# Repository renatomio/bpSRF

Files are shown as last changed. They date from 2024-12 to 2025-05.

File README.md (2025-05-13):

# bpSRF: An extra robotic finger powered by wrist movements
 Github site for the bpSRF, a body-powered supernumerary robotic finger for hand augmentation that requires no electronic components.
## Project Overview
This guide introduces the assembly and operation of the **Body-Powered Supernumerary Robotic Finger (bpSRF)**. The bpSRF is an lightweight device designed to enhance users' grasping capabilities by controlling an additional robotic finger using wrist movements. Unlike conventional SRFs, the bpSRF eliminates the need for electronic components and relies solely on body-powered mechanisms.

<p align="center">
  The bpSRF
</p>

The device is particularly suited for helping people with hand impairments that limit finger but not wrist movements. It is also an excellent tool for healthy individuals seeking to explore additional degrees of freedom and novel hand grasping patterns. The bpSRF is easily manufacturable using 3D printing, making it a cost-effective and replicable solution.

<p align="center">
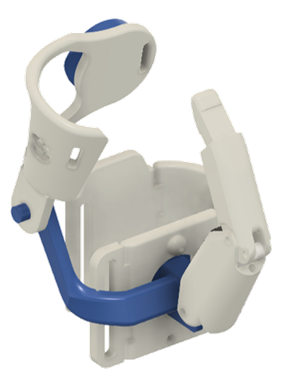
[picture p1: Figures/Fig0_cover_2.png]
  
</p>

Here are some examples on how it can be used:

<p align="center">
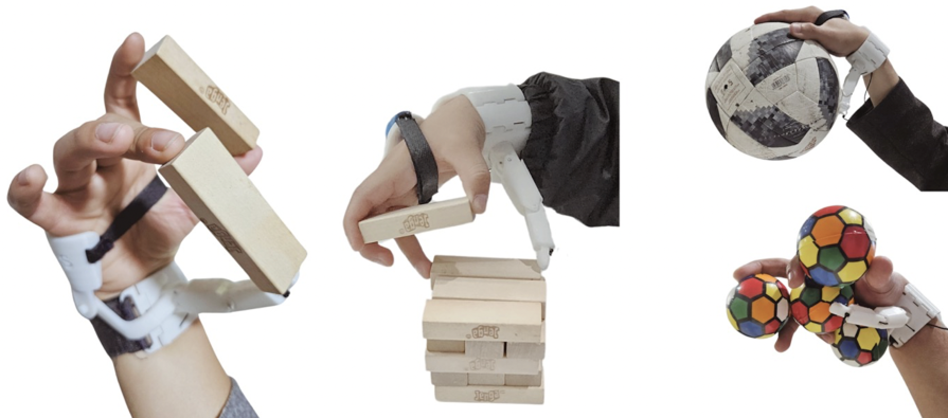
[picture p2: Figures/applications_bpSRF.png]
The bpSRF
  
</p>

<p align="center">
  The bpSRF
</p>

## Folder structure
The STL files are organized into folders as follows:
- **Finger**
    * Proximal phalanx
    * Distal phalanx
    * Inner link
- **Wrist**
    * Wrist side brace 1
    * Wrist side brace 2
    * Wrist buckle
    * Wrist posterior brace
    * Wrist anterior brace + driving link (in one part)
    * Shaft collar
- **Palm support**
    * Available in S, M and L sizes
- **Cable tensioner**
- **Fingertip**
    * Fingertip mold part 1
    * Fingertip mold part 2
    * Fingertip mold base

These last fingertip files are optional. They can be used in case you wish to add a silicon rubber fingertip to the bpSRF. These parts were designed as a mold in which liquid silicon rubber can be poured. The resulting silicon rubber fingertip perfectly matches the shape of the bpSRFs distal phalanx.

The following figure shows the different components of the bpSRF. Although not shown, the finger's inner link is inside the proximal phalanx and will be shown in the assembly guide.

<p align="center">
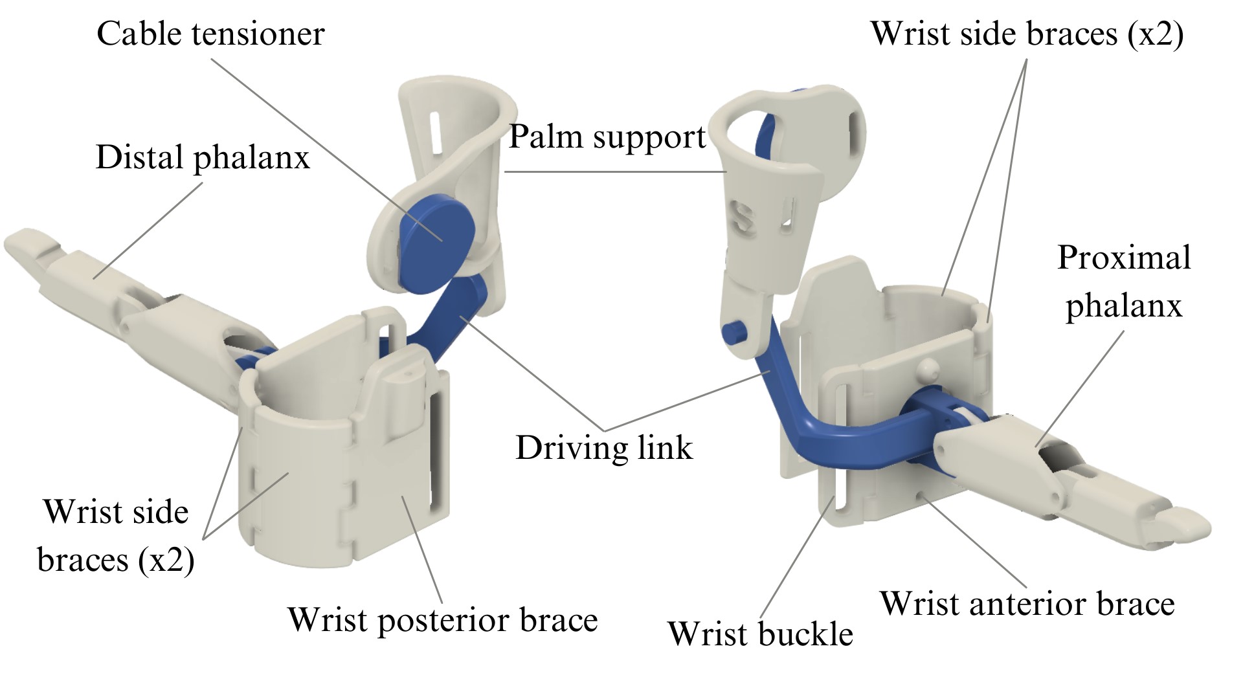
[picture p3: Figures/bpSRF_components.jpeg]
Components of the bpSRF
  
</p>

Each folder contains the parts required for printing. Please print one piece from each file in the respective folders.

## Getting Started
### Download the Files
Clone the repository or download the zip file to access all the STL files:

```bash
git clone https://github.com/RenatoMio/bpSRF.git
```
## Parameters for 3D-printing

The following are the recommended specifications for 3D-printing:

* Layer height: 0.2 - 0.24 mm
* Infill: 15%
* Print speed: 60 mm/s
* Support structure: Tree with 0% density (contours only)

The recommended orientations for printing the parts are as follows:

* **Finger components**
<p align="center">
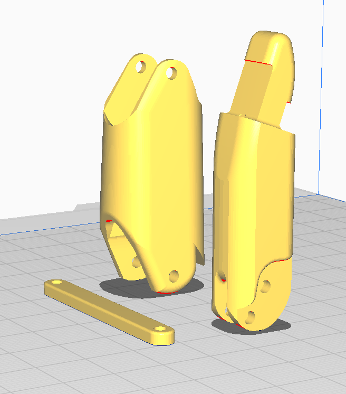
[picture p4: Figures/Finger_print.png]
  
</p>

* **Wrist components**

Take into account that the wrist anterior brace and driving link have a support blocker (shaded gray cube) to prevent the generation of support structures within internal tunnels, which would be impossible to remove.

<p align="center">
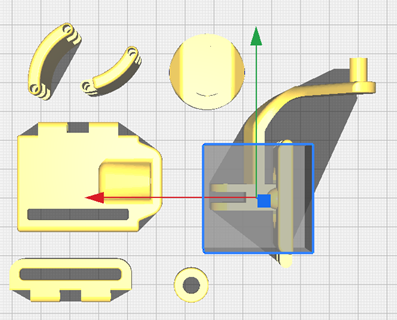
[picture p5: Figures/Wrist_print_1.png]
  
</p>

<p align="center">
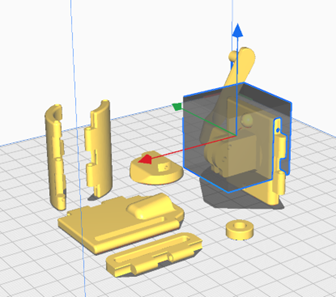
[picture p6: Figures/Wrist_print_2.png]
  
</p>

* **Palm support**
<p align="center">
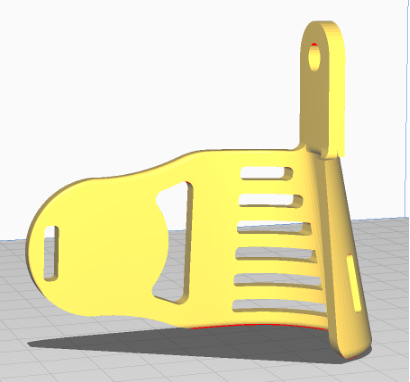
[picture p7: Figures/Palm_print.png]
  
</p>

A 3MF file containing the configurations and positions of the parts is available for rapid manufacturing on the Prusa MK3 printer. The print under the suggested parameters takes approximately 5.5 hours.

## Additional materials
To assemble the bpSRF, the following additional tools and materials are required.

### Tools

* Cutting pliers
* Needle-nose pliers
* Metal File Set
* Soldering iron
* Super glue

### 4. Materials
* 3D-printed components for the bpSRF (as listed in the folder structure)
<p align="center">
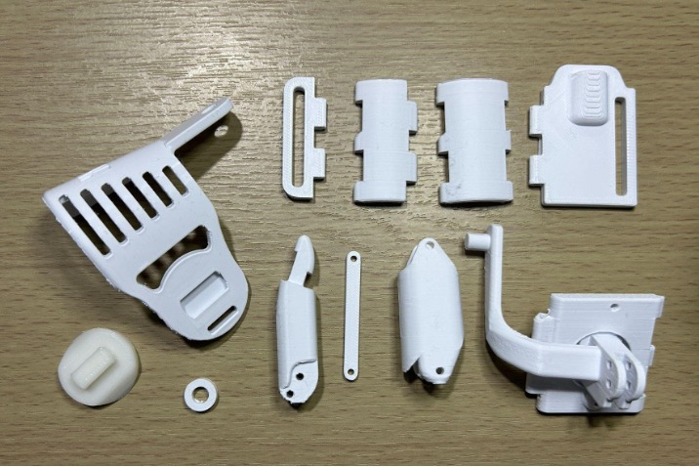
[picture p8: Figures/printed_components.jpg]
  
</p>

* Velcro straps:
    * 1.2 cm width and about 21 cm in length
    * 3.5 cm width and about 9 cm in length
* ⌀ 2.5 mm aluminum (or other metal) pins for joints in the following quantities and lengths:
    * 5 x 33 mm
    * 1 x 17 mm
    * 1 x 14 mm
    * 2 x 8 mm
* ⌀ 2 mm elastic wire
* ⌀ 0.25 mm rigid nylon wire
* OPTIONAL: Platinum silicone RTV-A20 A&B (or similar) for the fingertip.

<p align="center">
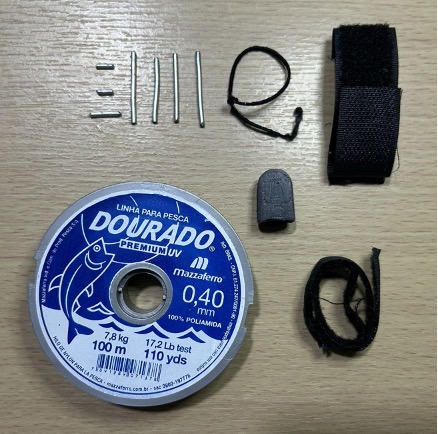
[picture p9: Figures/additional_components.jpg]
  
</p>

## Step-by-Step assembly instructions

### 1. Finger

Use the 8 mm pin to secure the inner link to the upper-most axis of the distal phalanx. Then, with the help of a soldering iron, we can slightly melt the plastic around the hole where the pin was inserted to prevent it from slipping out. Any other method to fixate it axially should also work.

<p align="center">
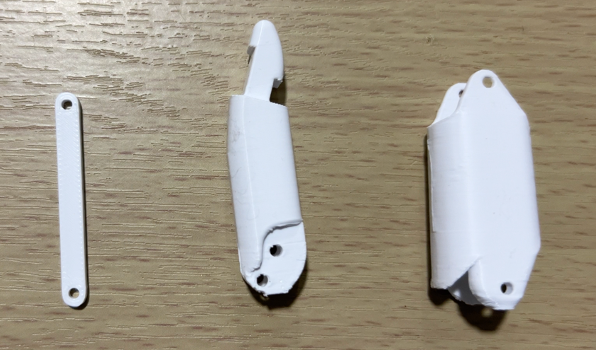
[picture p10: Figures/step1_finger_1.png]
  
</p>

<p align="center">
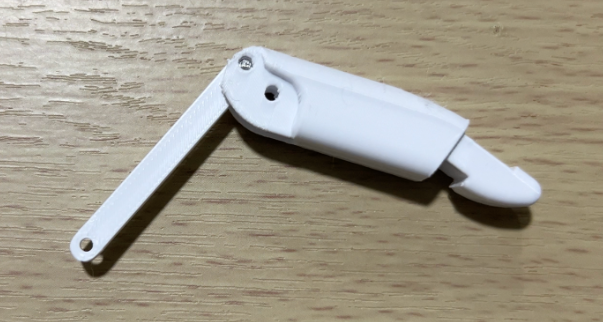
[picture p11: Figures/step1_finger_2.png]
  
</p>

Then, use the 17 mm pin to connect the distal phalanx with the proximal phalanx. We again ensure they do not slip by using a soldering iron to seal the hole. Another alternative to secure the shafts is to apply a drop of super glue.

<p align="center">
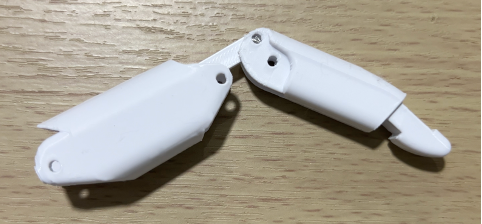
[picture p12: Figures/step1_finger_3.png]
  
</p>

<p align="center">
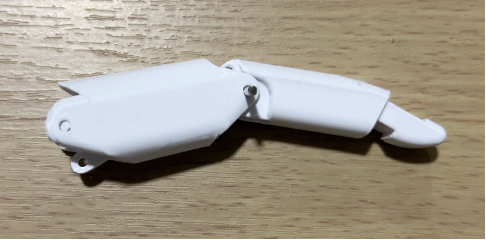
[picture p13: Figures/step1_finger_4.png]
  
</p>

Once assembled, verify that both phalanges and the inner link slide smoothly against each other, without any significant friction.

Is best to try the assembly without glueing first and, if there was any high friction between surfaces, these should be smoothed using the metal files.

### 2. Wrist bracelet

Next, attach the finger to the wrist using the 17 mm and 8 mm pins. The longer pin joins the proximal phalanx while the shorter connects the inner link to the palm.

<p align="center">
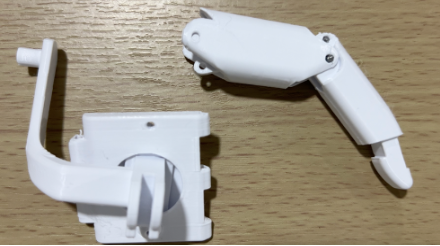
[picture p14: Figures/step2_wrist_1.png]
  
</p>
<p align="center">
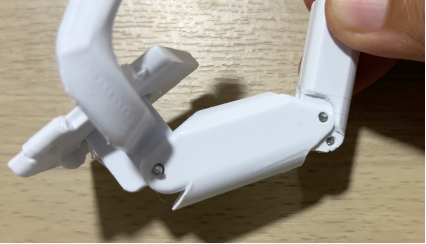
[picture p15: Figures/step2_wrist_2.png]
  
</p>

For the wrist braces, we will use the 33 mm pins. First, we connect the wrist buckle to the wrist anterior brace by passing the pin through the hole located at the bottom of the pieces.

<p align="center">
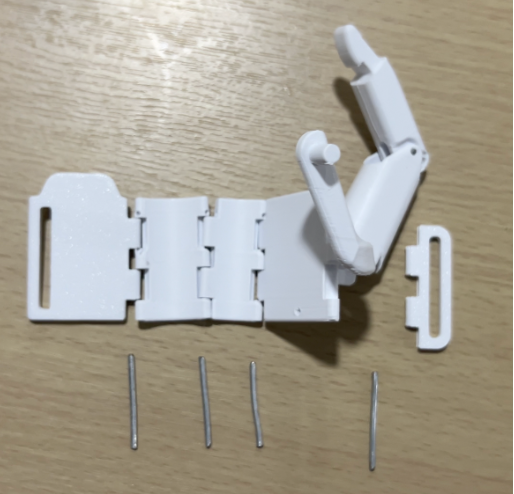
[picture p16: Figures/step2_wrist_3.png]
  
</p>

Before attaching the other wrist braces, pass the rigid nylon wire through the sphere of the wrist anterior brace and through the wrist side brace 1. Then, pass the pin through the hole to connect the wrist side brace 1 to the wrist anterior brace.
Next, add the wrist side brace 2 to the connection by passing the rigid nylon wire through it. Then, pass the pin through the hole to secure it.

Finally, attach the wrist posterior brace to the entire assembly by passing the rigid nylon wire through and securing it with the pin through the hole.

<p align="center">
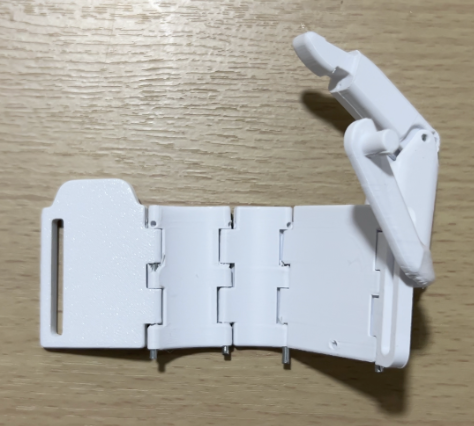
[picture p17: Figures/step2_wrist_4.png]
  
</p>

Using the 3.5 cm Velcro strap, pass it through the hole of the wrist posterior brace and sew it to ensure it is securely fixed.

<p align="center">
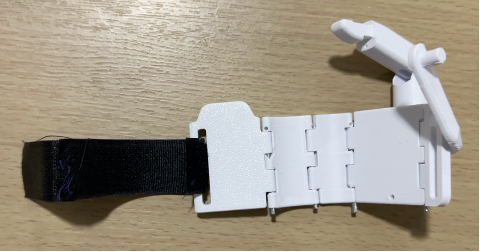
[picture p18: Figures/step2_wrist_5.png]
  
</p>

<p align="center">
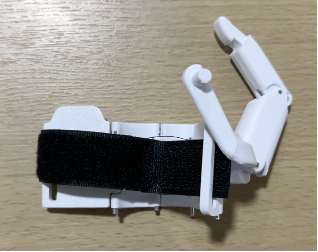
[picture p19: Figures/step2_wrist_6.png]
  
</p>

### 3. Palm support

The palm support holds the cable tensioner for the nylon cable and needs to be fixed to the wrist’s anterior brace.

<p align="center">
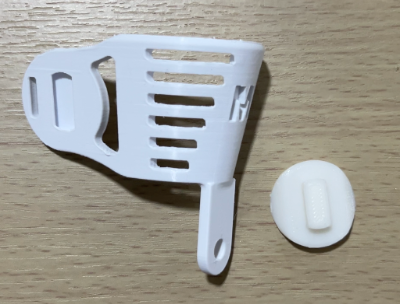
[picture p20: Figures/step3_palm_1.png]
  
</p>

<p align="center">
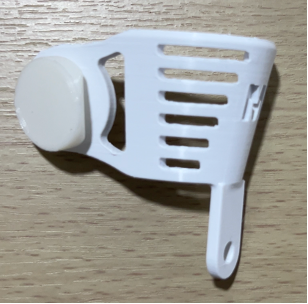
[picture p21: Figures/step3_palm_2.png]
  
</p>

The shaft collar is placed on the outer surface of the rotational axis of the palm support, to prevent it from moving axially.

<p align="center">
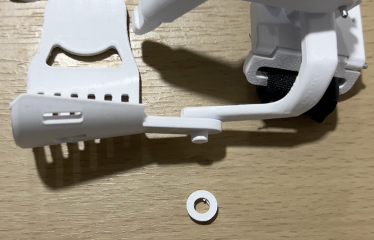
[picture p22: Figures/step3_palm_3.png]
  
</p>

<p align="center">
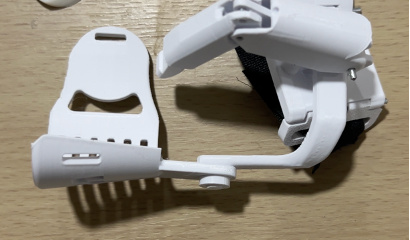
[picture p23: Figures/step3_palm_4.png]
  
</p>

Using the 1.2cm-width Velcro strap, glue or sew it onto the slot on the side of the palm support to secure that end.

<p align="center">
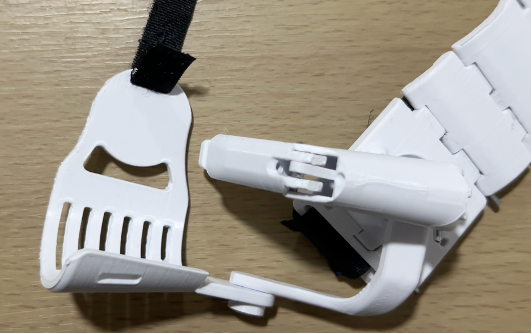
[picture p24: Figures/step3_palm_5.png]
  
</p>

### 4. Securing the elastic wire

Tie the ⌀2mm elastic wire at the tip of the distal phalanx. Once it is securely tied, we pass it through the upper holes of the distal and proximal phalanx.  
In the wrist anterior brace, you will find a hole through which the elastic wire should be passed and tied to ensure it is secure. The elastic wire should be stretched enough to allow the finger to return to its initial position.

<p align="center">
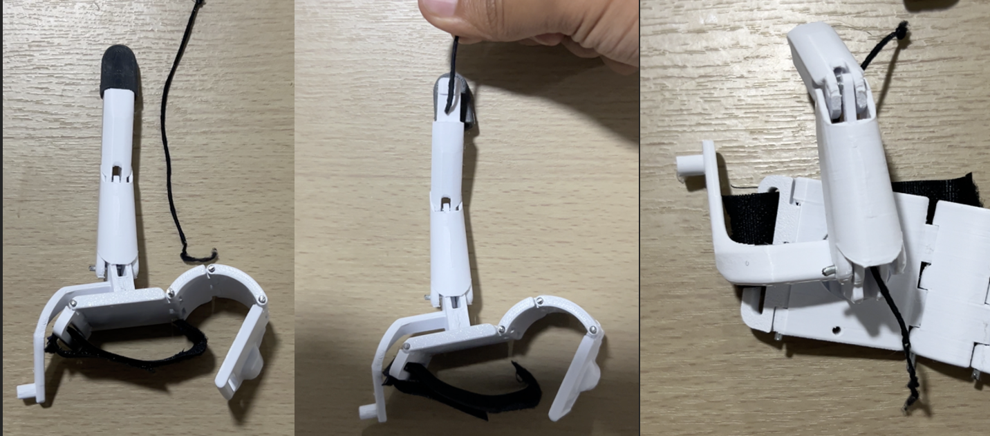
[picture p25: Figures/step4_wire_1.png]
  
</p>

Similarly, we tie the rigid nylon wire at the tip, then pass it through the lower holes of the distal and proximal phalanx, respectively.

<p align="center">
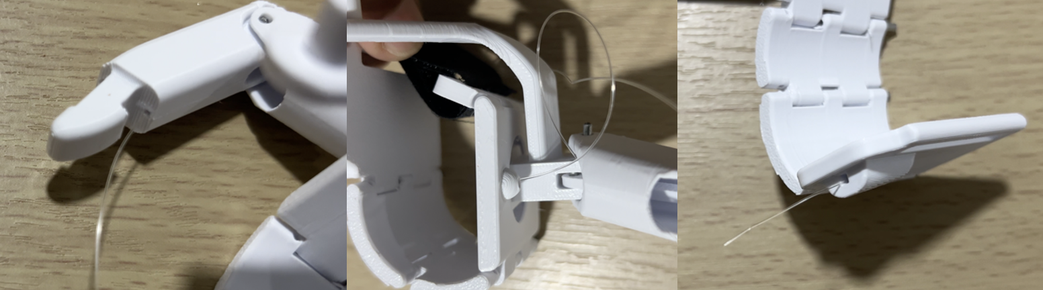
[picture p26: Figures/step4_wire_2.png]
  
</p>

### 5. Securing the rigid nylon

The ⌀0.25mm rigid nylon wire that drives the finger flexion must be connected to the cable tensioner. Tie it with at least 3 knots to ensure it stays secure. The remaining length between the cable tensioner and the exit point of the nylon wire from the wrist posterior brace should be at least greater than 8 cm. This length depends on the size of the hand.

<p align="center">
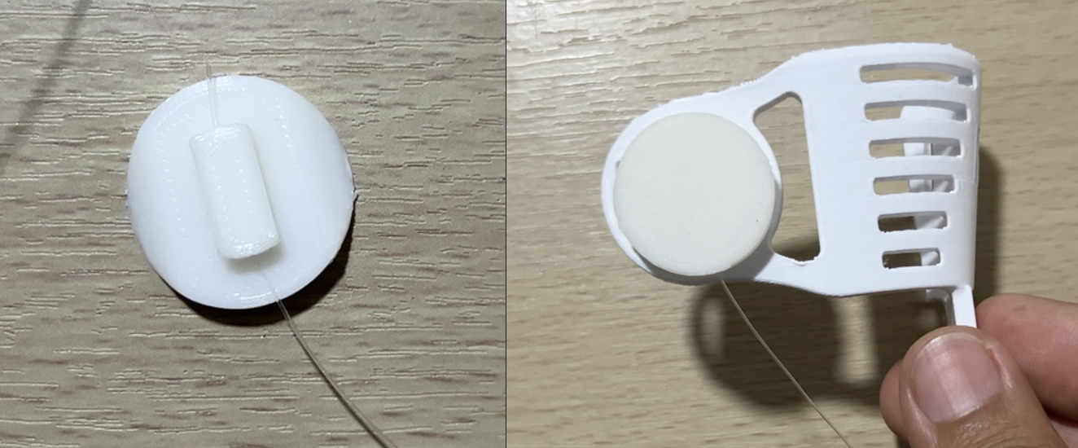
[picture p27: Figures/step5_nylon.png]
  
</p>

### Extra: Add a silicon rubber fingertip

The silicone mix is prepared by mixing around 6 grams of both components of the RTV-A20 silicone in a 50/50 ratio. Once mixed, these components will solidify in less than an hour. Note that other liquid silicone rubbers, such as those that use a catalyst for solidifying, would also work.

Using a plastic stick or any similar tool, the silicone is stretched to remove air bubbles and then poured into the mold.

<p align="center">
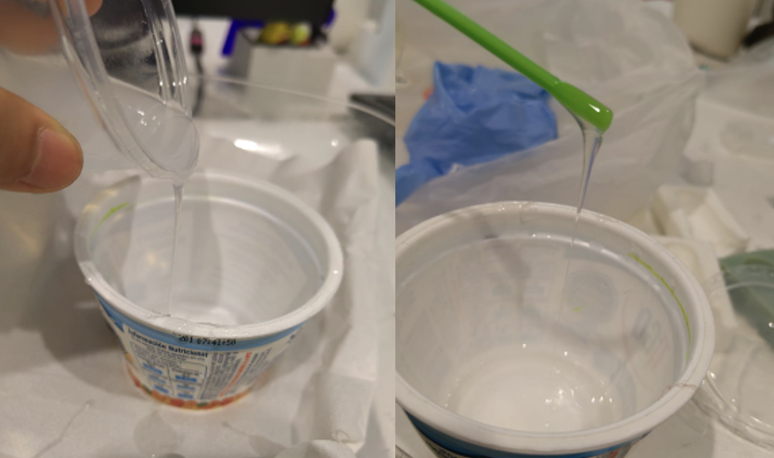
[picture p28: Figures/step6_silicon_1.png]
  
</p>

Both sides of the mold should enclose the mold base, shaped after the SRF's finger. After pouring the material, the parts are secured using zip ties and left to rest for 45 minutes. Finally, the mold is removed, and it is placed onto the finger of the bpSRF.

<p align="center">
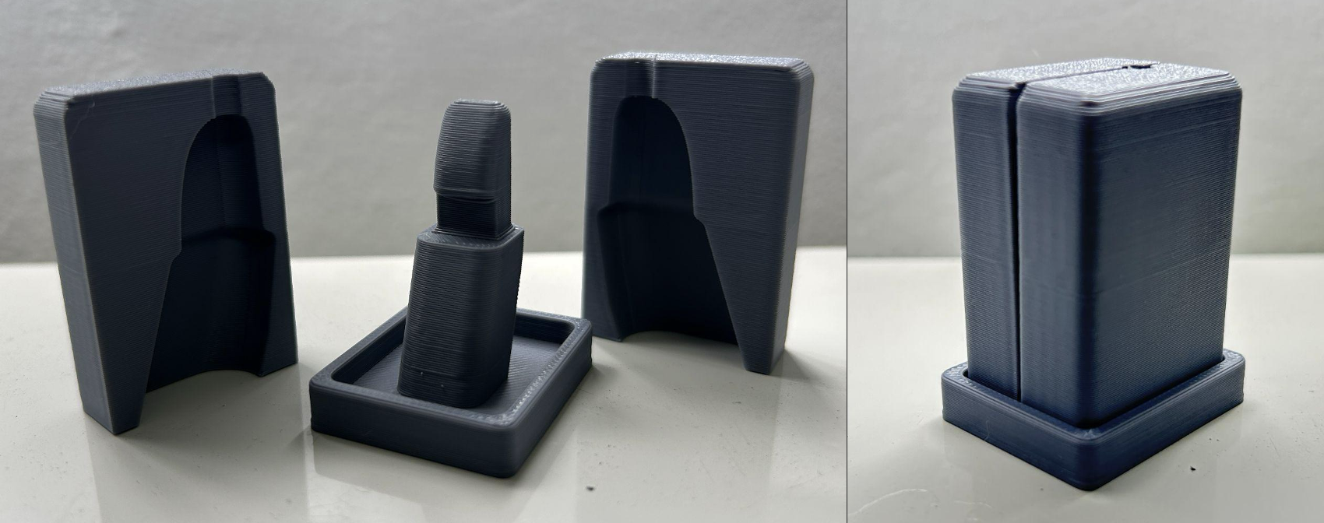
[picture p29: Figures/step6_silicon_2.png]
  
</p>

After solidifying, the fingertip can be removed from the mold. The fingertip should be placed over the top of the finger’s distal phalanx to add compliance and added friction. This helps prevent slipping during object grasping.
<p align="center">
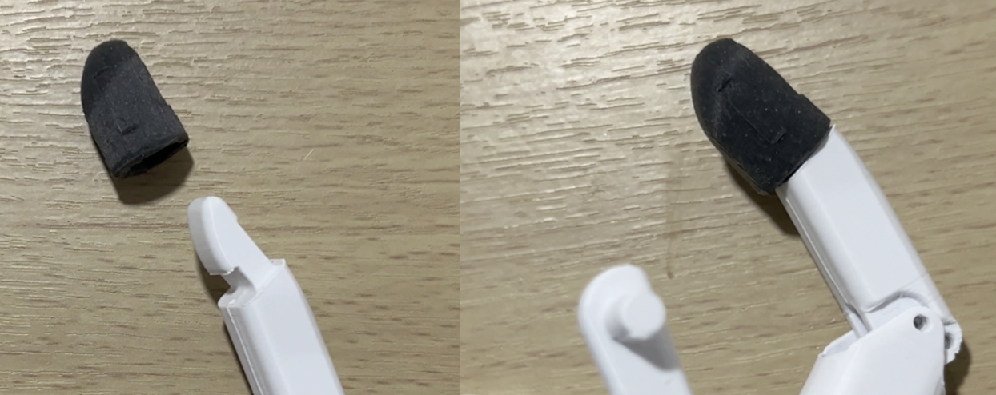
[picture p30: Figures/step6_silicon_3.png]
  
</p>

That's it! You can start wearing and trying out the bpSRF. Some cable tensioning or tweaking might still be needed.

Here you can see the basic donning:

<p align="center">
  The bpSRF
</p>

And the cable tensioning procedure:

<p align="center">
  The bpSRF
</p>

<!---
## Contributors

This project was a collaborative effort. Below is a summary of contributions:

- **Renato Mio**: Project conceptualisation, co-developing of the design, experimental protocols design, and data analysis.
- **Alyssa N. Maguina**: Co-developing of the design, conducting of experiments, and data analysis.
- **Sebastián Caballa**: Mechanical validation tests and analyses.

--->

## License

This project is licensed under the [Creative Commons Attribution-NonCommercial-ShareAlike 4.0 International License](https://creativecommons.org/licenses/by-nc-sa/4.0/).  
You are free to:
- Share: Copy and redistribute the material in any medium or format.
- Adapt: Remix, transform, and build upon the material.  

**Under the following terms**:
- **Attribution**: You must give appropriate credit, provide a link to the license, and indicate if changes were made.
- **NonCommercial**: You may not use the material for commercial purposes.
- **ShareAlike**: If you remix, transform, or build upon the material, you must distribute your contributions under the same license as the original.

For more details, see the full license text in the `LICENSE` file.

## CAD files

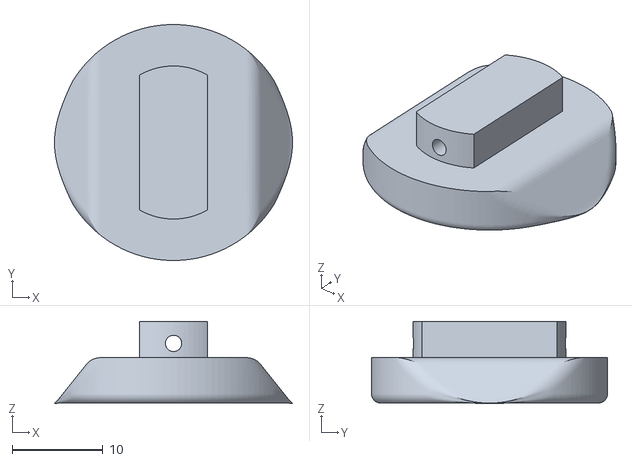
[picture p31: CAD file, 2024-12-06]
STLs/CableTensioner.stl
26.2 x 26.0 x 9.07

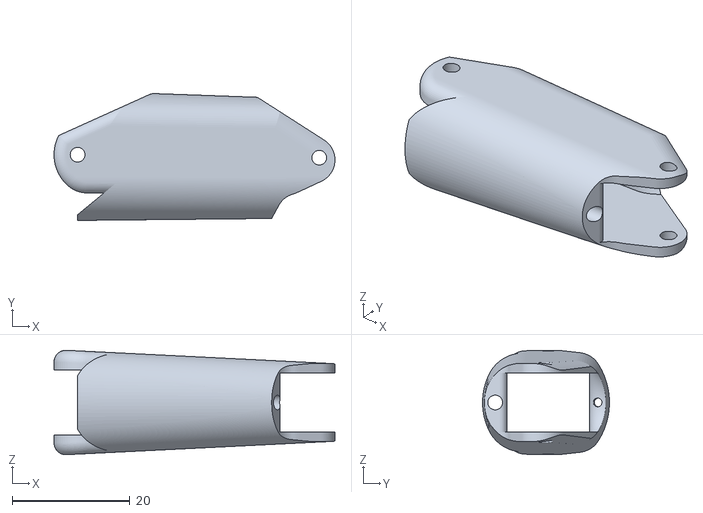
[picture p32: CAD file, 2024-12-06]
STLs/Finger/ProximalPhalanx.stl
47.7 x 21.5 x 17.7

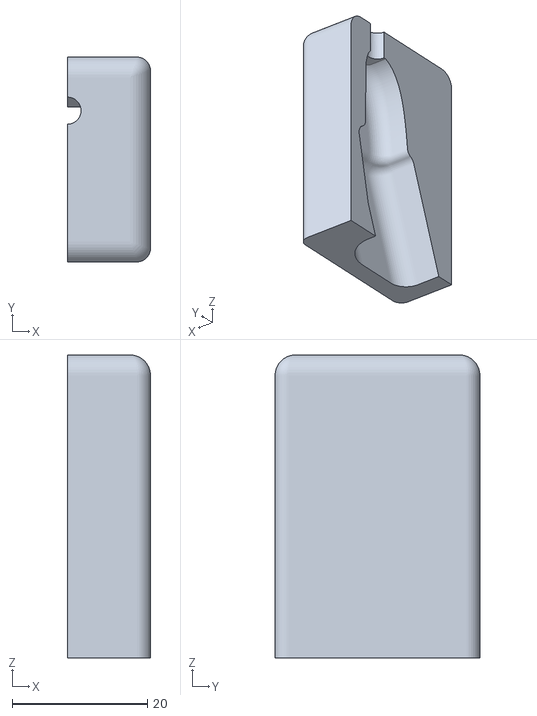
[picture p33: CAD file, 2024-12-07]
STLs/Fingertip/FingertipMold_p2.stl
12.2 x 30.2 x 44.8

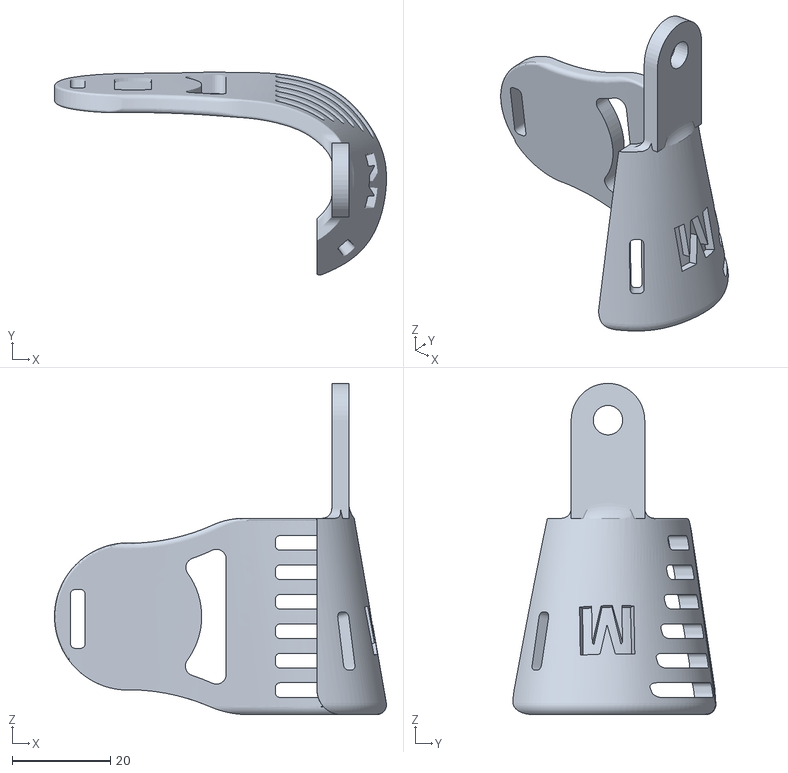
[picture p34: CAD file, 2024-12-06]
STLs/Palm support/PalmSupport_M.stl
67.6 x 41.3 x 67.5

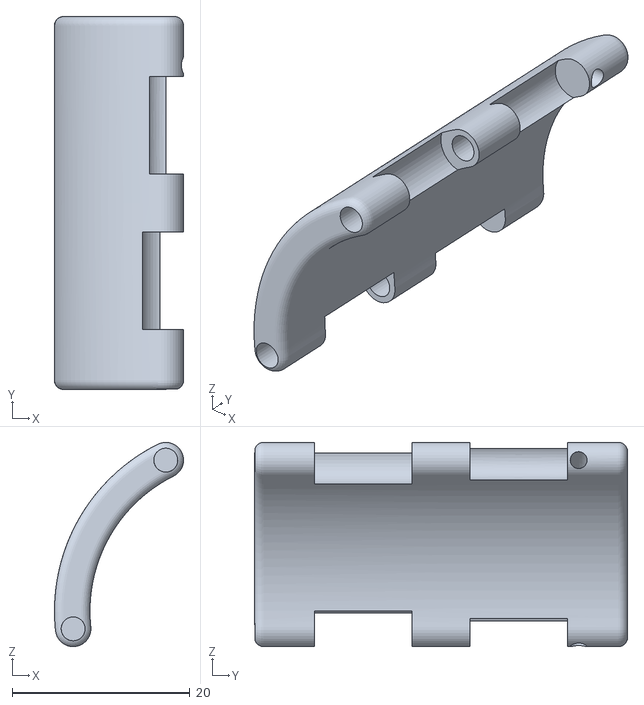
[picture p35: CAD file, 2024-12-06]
STLs/Wrist/WristSideBrace2.stl
14.5 x 42.0 x 23.0

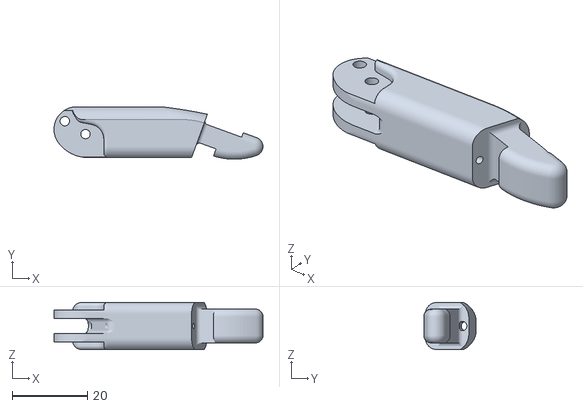
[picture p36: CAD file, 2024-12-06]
STLs/Finger/DistalPhalanx.stl
55.5 x 13.9 x 12.5

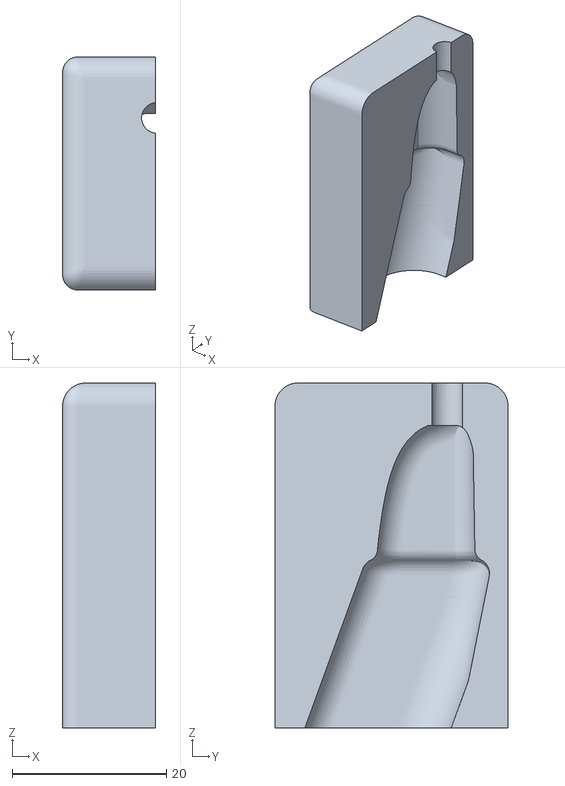
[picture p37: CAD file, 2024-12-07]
STLs/Fingertip/FingertipMold_p1.stl
12.0 x 30.2 x 44.8

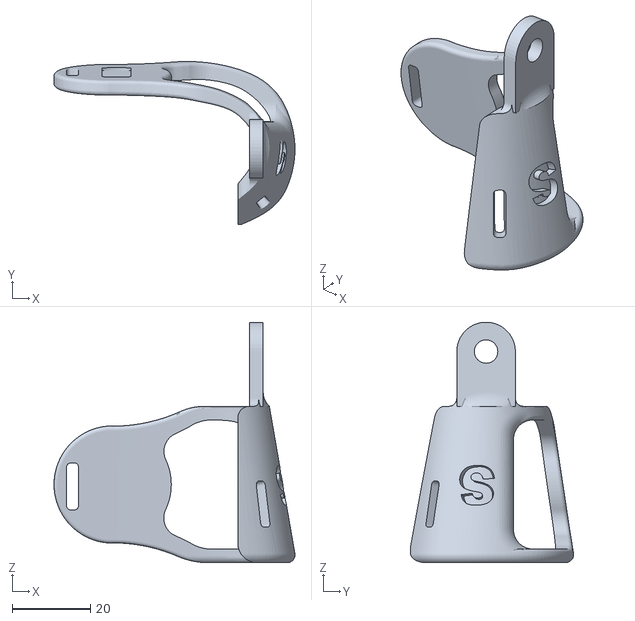
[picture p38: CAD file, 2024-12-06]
STLs/Palm support/PalmSupport_S.stl
61.6 x 41.8 x 61.5

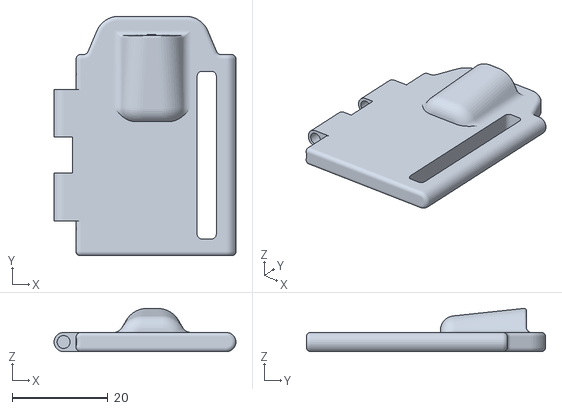
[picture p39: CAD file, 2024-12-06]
STLs/Wrist/WristPosteriorBrace.stl
38.0 x 50.0 x 9.01

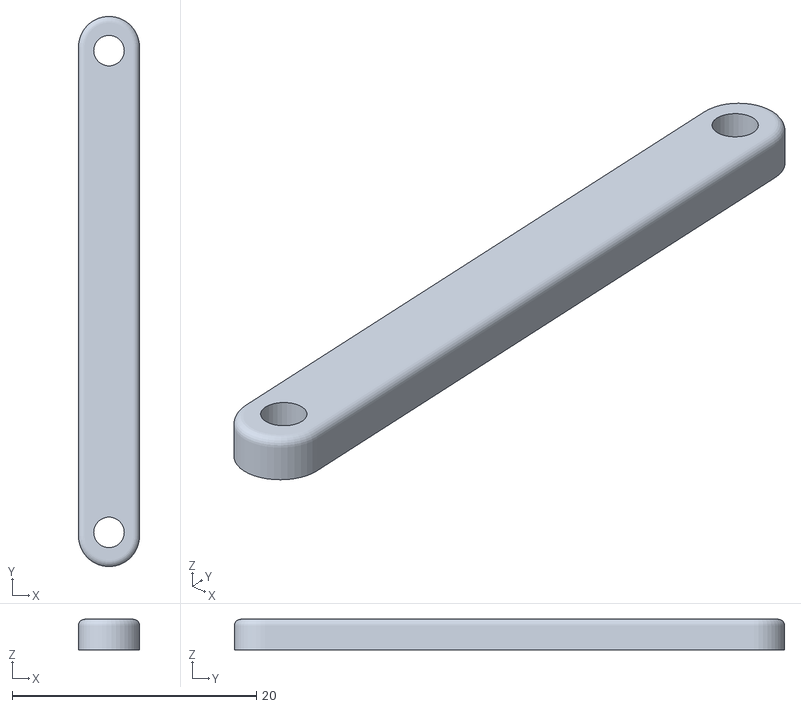
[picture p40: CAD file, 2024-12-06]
STLs/Finger/InnerLink.stl
5.00 x 45.0 x 2.50

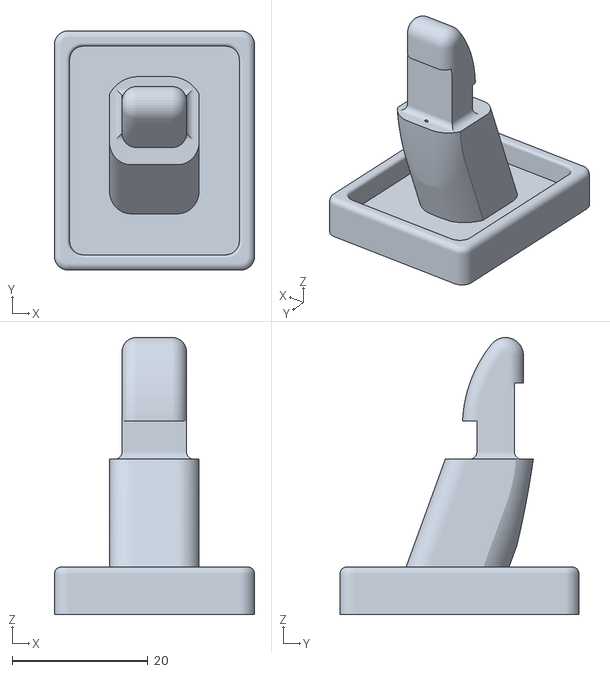
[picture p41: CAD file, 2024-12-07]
STLs/Fingertip/FingertipMold_base.stl
29.5 x 35.2 x 40.8

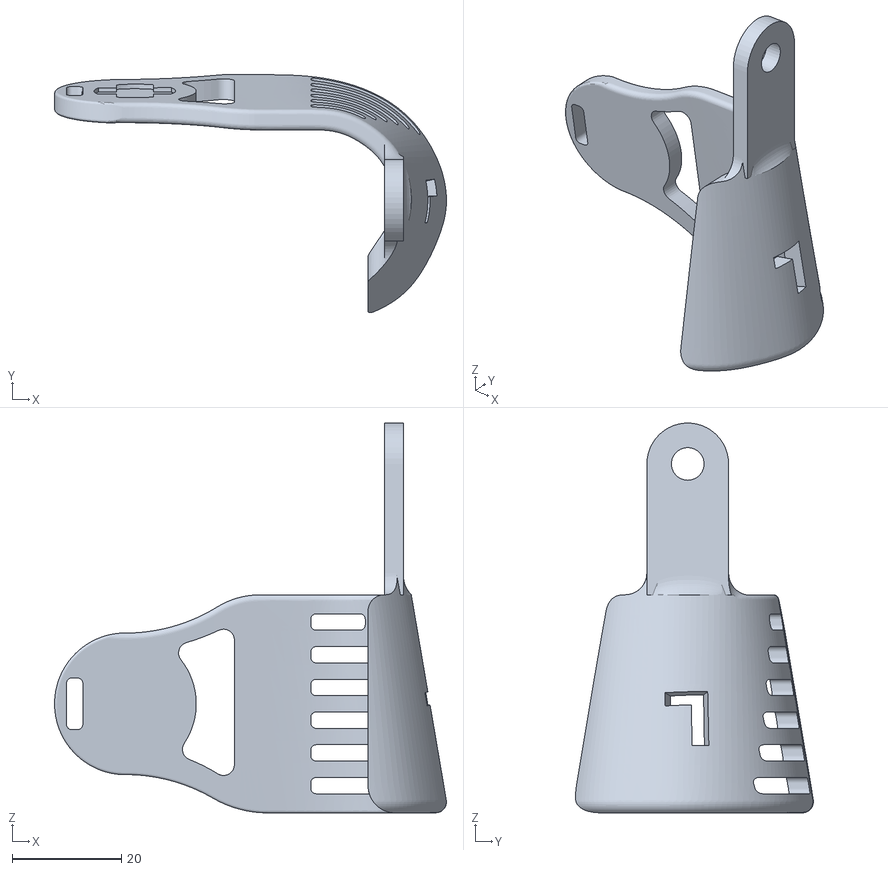
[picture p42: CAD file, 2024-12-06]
STLs/Palm support/PalmSupport_L.stl
71.9 x 43.6 x 71.5

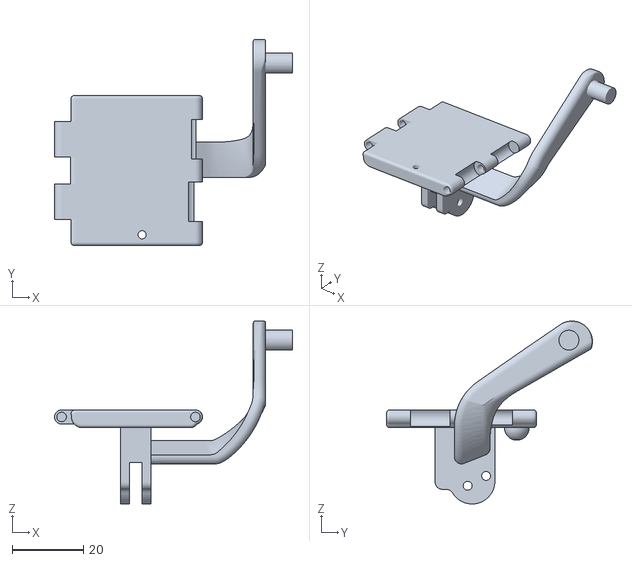
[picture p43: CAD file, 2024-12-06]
STLs/Wrist/WristAnteriorBrace_w_DrivingLink.stl
66.7 x 57.7 x 51.3

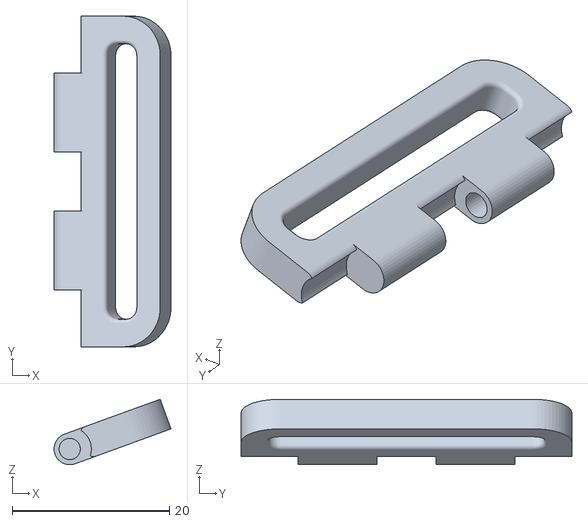
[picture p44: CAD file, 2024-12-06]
STLs/Wrist/WristBuckle.stl
14.9 x 42.0 x 8.31

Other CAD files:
STLs/Wrist/ShaftCollar.stl
STLs/Wrist/WristSideBrace1.stl

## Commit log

2024-12-06 First complete version, might need small corrections later or better images
    [CableTensioner.stl, DistalPhalanx.stl, InnerLink.stl, PalmSupport_L.stl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]
2024-12-07 first version completed
    [CableTensioner.stl, DistalPhalanx.stl, FingertipMold_base.stl, FingertipMold_p1.stl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]
